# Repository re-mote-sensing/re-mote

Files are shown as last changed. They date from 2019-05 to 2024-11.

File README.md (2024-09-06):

<div align="center">
    <h1>re:mote</h1>
    <p>Open-source Low-cost Software and Hardware Infrastructure for Remote Sensing</p>
</div>

## 📎 Table of Contents

1. [About re:mote](#-about-remote)
2. [LoRa & Mesh Network](#-lora--mesh-network)
3. [Setup](#-get-started)
    - [Water Quality Sensing](#setup-water-quality-sensing)
    - [Turtle Tracker](#setup-turtle-tracker)
4. [Documentation](#-documentation)
5. [Acknowledgement](#-acknowledgment)

## 📒 About re:mote

### Low-cost Water Quality Sensing and Turtle Tracking

This is a software and hardware infrastructure for long-term monitoring of water quality parameters and seasonal monitoring of turtle movements that normally cost a lot more to make, but you can do it by yourself at a fraction of the price compared to commercial products. It supports various configurations, including different sensors, network options, and enclosures, making it adaptable to diverse environments. Designed for low power consumption for 3 months using 6 AA batteries, it can be deployed in a remote area with limited cell connection.

<div align="center">
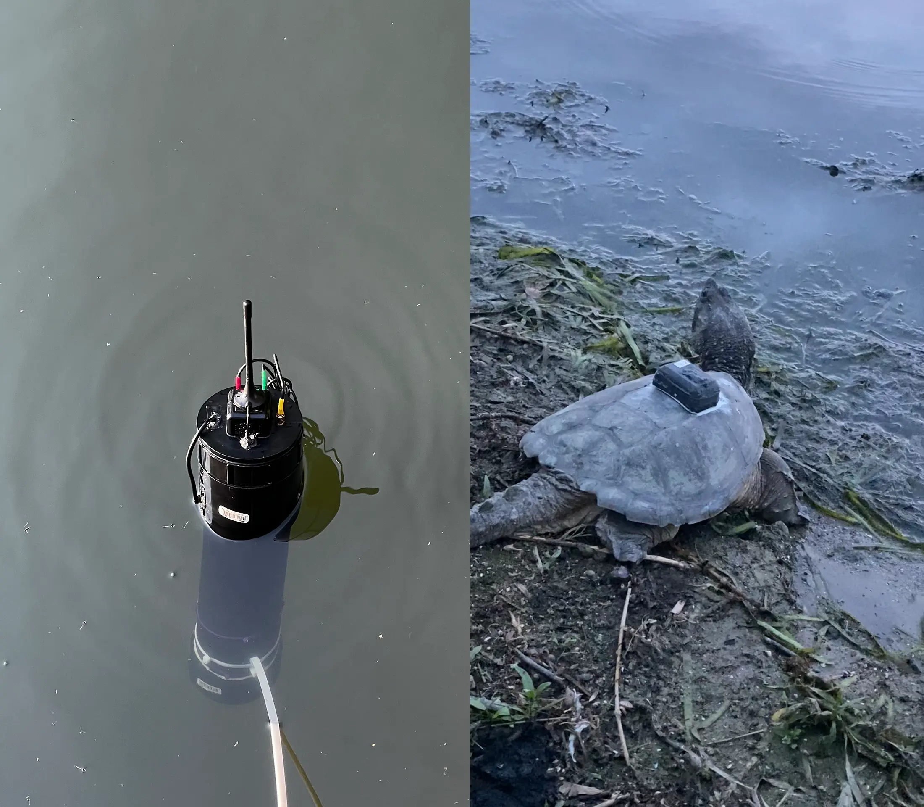
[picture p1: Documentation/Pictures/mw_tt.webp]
    
    <p>Working Water Sensor / Turtle Tracker</p>
</div>

---

## 🛰 LoRa & Mesh Network

### Low-power long-range sensor network

A LoRa mesh network is optionally used for connecting motes (motes can operate standalone).
- It is a low-bandwidth, low-power, and long-range network.
- The mesh network is tolerant to faults, changing network topology, extension, and contraction.

<div align="center">
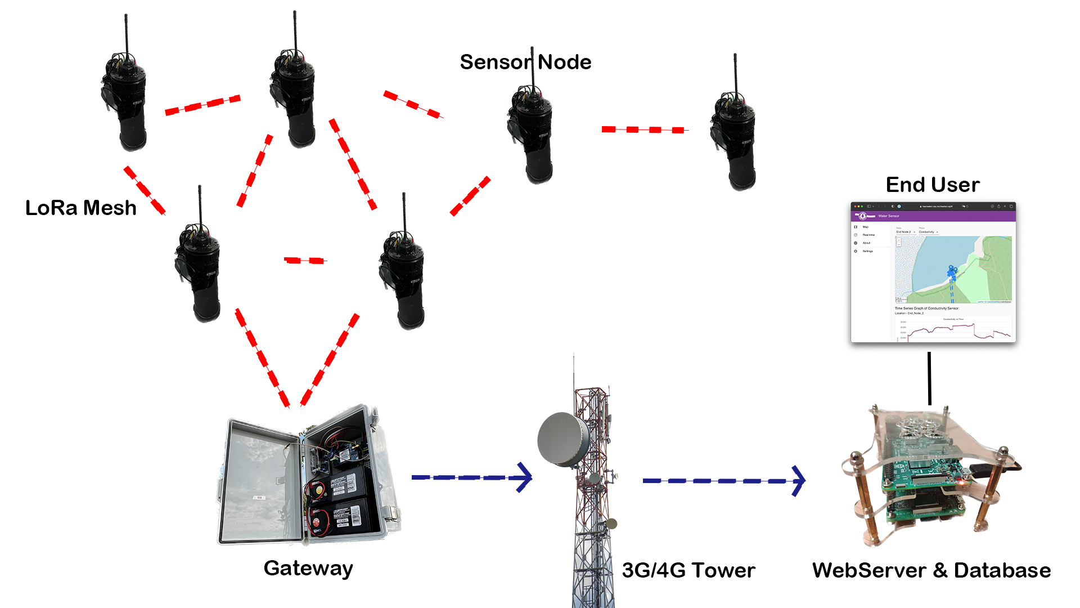
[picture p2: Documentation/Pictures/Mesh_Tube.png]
    
</div>

### Motes

- Mote is an old term for an IoT device which is connected to the network.

Water monitoring network:
- **Gateway** (one or multiple) to relay motes data to the server over the
internet using a CAT-M1/NB-IoT/LTE/3G connection.
- **End Motes** (one or multiple) to measure water quality parameters through attached sensors.
    - **pH** sensor shows the acidity or alkalinity, helping to detect imbalances.
    - **Conductivity** sensor reveals the amount of salts present, providing insight into water quality.
    - **Dissolved Oxygen** sensor measures oxygen levels in the water, indicating the health of aquatic life.
    - **Water Temperature** sensor helps calibrate all sensor levels.
    - **Turbidity** sensor indicates water clarity, with changes signalling potential disturbances.
    - **[Custom sensors](/Documentation/Water_Sensor/Custom_Sensors.md)**

### Server

For real-time monitoring, the Raspberry Pi is an affordable option. However, a regular PC can also be utilized if preferred.

The server is programmed in Golang for fast and concurrent connections.
- A progressive web application designed in React with a custom API.
    - A Progressive Web Application (PWA) enables you to access and browse your data conveniently on your phone.
    - A custom API facilitates easy integration with various other systems.
- A time-series database (InfluxDB) for simple data storage and a smaller footprint. Time series databases assume that insertions are more frequent than queries, so it allows for the fast insertion of large amounts of data, such as water quality data. [Learn More](https://gitlab.cas.mcmaster.ca/re-mote/publications/-/tree/master/FadhelSekerinskiYao18Timeseries)

## 🚀 Get started

This list will guide you step by step to get started.

---

### Setup [Water Quality Sensing](Water_Sensor/)

1. Get all the [hardware](/Documentation/Water_Sensor/Specification.md) you need.

2. Setup a water sensor server with one of the options below. They perform with the same functionality, with docker you do not need to configure all dependencies and run on your own server or computer.
    - Install water sensor server on [Docker](Water_Sensor/re-mote-webserver/). **(Recommended)**
    - Install water sensor server on [Linux](/Documentation/Water_Sensor_Server/Server_Instructions.md).
    - Install water sensor server on a [cloud service](https://gitlab.cas.mcmaster.ca/re-mote/publications/tree/master/HuangMengqi19Encryption&Storage).

3. Assembly of Hardware for the [SensorMotes and/or Gateways](/Documentation/Water_Sensor/Build_a_Water_Sensor_Portal.md).

4. [Testing and Deploying](/Documentation/Water_Sensor/Build_a_Water_Sensor_Portal.md#testing).

---

### Setup [Turtle Tracker](Turtle_Tracker/)

1. Get all the [hardware](Turtle_Tracker/Docs/Specification.md) you need.

2. Setup a water sensor server with one of the options below.
    - Install water sensor server on [Linux](/Documentation/Water_Sensor_Server/Server_Instructions.md) with the [source code](Turtle_Tracker/turtle-tracker-webserver).
    - Install turtle tracker server on a [cloud service](https://gitlab.cas.mcmaster.ca/re-mote/publications/tree/master/HuangMengqi19Encryption&Storage).

3. Assemble Hardware and Upload the Firmware for [Tracker](Turtle_Tracker/Docs/Assembly_of_Trackers.md) and [Gateway](Turtle_Tracker/Docs/Assembly_of_Gateway.md).

---

### Get help

- If you have any questions or encounter issues, post them [here](https://github.com/re-mote-sensing/re-mote/issues).

## 🗂 Documentation

- For developers only.

 - Water Sensor
    - End Mote & Gateway
        - [LoRa message format](/Documentation/Water_Sensor/Message_Formats.md)
        - [Saved data formats](/Documentation/Water_Sensor/Saved_Data_Formats.md)
        - [Add custom sensors](/Documentation/Water_Sensor/Custom_Sensors.md)
    - Server
        - [Jupyter analysis](Jupyter_Analysis/)
        - [REST api](https://documenter.getpostman.com/view/5847961/2s83tDpshb)
        - [Database format](/Documentation/Water_Sensor_Server/Database_Format.md)
 - Turtle Tracker
    - End Mote & Gateway
        - [LoRa message format](Turtle_Tracker/Docs/message_format_turtle_tracker.xlsx)
 - Research
    - [Research documents](Research/)

## 🏆 Acknowledgment

[McMaster University](https://www.mcmaster.ca)

[Global Water Futures](https://gwf.usask.ca)

[MacWater](http://www.macwater.org)

[Ontario Research Fund](https://www.ontario.ca/page/ontario-research-fund)

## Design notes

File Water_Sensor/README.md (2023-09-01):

# re:mote | Water Sensor

## Arduino

`./Node_Code/Node_Code.ino` is the main arduino-based motes firmware.

`./Libraries/` are required libraries for motes.

## Server

`./re-mote-webserver` is the server program running on your PC or cloud service to provide real-time motinoring.

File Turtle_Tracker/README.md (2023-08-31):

turtle

# Turtle Tracker Overview

Code used in the Turtle Tracker project, 2022 version. This version differs from the previous version located in `Node_Code.ino`.

## Arduino Code

`./Arduino_Code/Gateway_Code/` is for use with the Gateway module which consists of an Arduino UNO, LoRA shield, 3G Shield and SD Card Reader.

`./Arduino_Code/Tracker_Code/` is for use with the Turtle Tracker module which consists of a Moteino (RFM95) and GPS module.

## Documentations

 - [Hardware Specification](./Docs/Specification.md)

###### Setup:

 - [Assembly of Gateway](./Docs/Assembly_of_Gateway.md)

 - [Assembly of Trackers](./Docs/Assembly_of_Trackers.md) | [Trackers Enclosure](./Docs/3D_Printed_Enclosure/README.md)

 - [Pi Server Source Code](./turtle-tracker-webserver) | [How to Setup Server](/Documentation/Water_Sensor_Server/Server_Instructions.md)

###### Code:

 - [Message Format](./Docs/message_format_turtle_tracker.xlsx)

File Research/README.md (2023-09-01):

# Research Projects
## AnjaliNarayanan18
Testing code on temperature and turbidity sensors.
## HassanElaghoury18
Testing code on LoRa mesh network.
## LoRa
Selection of LoRa modules, LoRa range test and testing code on LoRa mesh network.
## MingzheAES
Research on AES Encryption
## Ryan_Notes
Notes on turtle tracker (GPS, LoRa, Antenna, Microcontroller, Enclosure).
## Server_design
Server design notes

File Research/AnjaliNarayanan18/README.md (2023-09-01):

Testing code on temperature and turbidity sensors.

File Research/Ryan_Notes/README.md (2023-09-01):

Notes on turtle tracker (GPS, LoRa, Antenna, Microcontroller, Enclosure).

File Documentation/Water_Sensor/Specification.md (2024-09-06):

# Specification for Water Quality Sensing

## Server Node

Raspberry Pi is the inexpansive option, any PC that runs Docker can be used (Windows, Linux, MacOS).

| Part           | Link                                                         |
| -------------- | ------------------------------------------------------------ |
| Raspberry Pi 4 | https://www.raspberrypi.com/products/raspberry-pi-4-model-b/ |
| SD card 32 GB *  | https://www.amazon.ca/gp/product/B08GY9NYRM/                 |

* You have the flexibility to use various SD cards; here's an example for reference.

<br><br>

## Water Sensor End Node

| Part                            | Link                                                               |
| ------------------------------- | ------------------------------------------------------------------ |
| Arduino Mega                    | https://www.amazon.ca/gp/product/B01H4ZDYCE/                       |
| MicroSD Card *                  | https://www.amazon.ca/gp/product/B08J4HJ98L/                                     |
| MicroSD Card Reader Module      | https://www.amazon.ca/gp/product/B07GXBP672/                                     |
| AA Battery Holder (3 x 1.5v) *  | https://www.amazon.ca/gp/product/B07PJT5NHL/                       |

* You're not limited to a specific SD card; here's an example for your consideration. However, it's essential to note that the SPI card reader lacks error correction. To mitigate potential issues, opt for a reputable, high-quality brand.
* You can explore alternative battery options, provided the voltage falls within the 4.5 to 5.5V range.

| Part                            | Link                                                               |
| ------------------------------- | ------------------------------------------------------------------ |
| GPS Receiver - GP-735           | https://www.sparkfun.com/products/13670                            |
| JST connector (for GPS)         | https://www.digikey.ca/en/products/detail/sparkfun-electronics/PRT-10361/6605206 |

* GPS is optional, if you prefer to enter coordinates by yourself

## Sensors

| Part                    | Link                                                               |
| ----------------------- | ------------------------------------------------------------------ |
| Conductivity Kit        | https://atlas-scientific.com/kits/conductivity-k-0-1-kit/          |
| Dissolved Oxygen Kit    | https://atlas-scientific.com/kits/dissolved-oxygen-kit/            |
| Turbidity Sensor        | https://www.dfrobot.com/product-1394.html                          |
| Temperature Sensor Kit  | https://www.dfrobot.com/product-1354.html                          |
| Industrial pH Probe<br><br>EZO™ Carrier Board for pH<br><br>EZO™ pH Circuit     | https://atlas-scientific.com/probes/industrial-ph-probe/<br><br>https://atlas-scientific.com/carrier-boards/electrically-isolated-ezo-carrier-board-gen-2/<br><br>https://atlas-scientific.com/embedded-solutions/ezo-ph-circuit/|

- It's recommended to use one or more specified sensors. However, if you opt for alternative sensors, be aware that programming skills are necessary for proper integration.

### Additional Hardware
Depending on your network preference, select one of the options provided below.

---

<details>
<summary>Using LoRa with one or more gateways</summary>
<br>

This approach employs a mesh network, ideal for situations where the 3G signal is unstable or unavailable over water.

<div align="center">
    
</div>

A gateway is essential to facilitate the transmission of data from the node to the server.

## Water Sensor End Node with **LoRa** Additional Components

| Part                    | Link                                                               |
| ----------------------- | ------------------------------------------------------------------ |
| Mesh LoRa [YL-800N Datasheet](/Documentation/Datasheets/LoRa_MESH_Radio_YL-800N_EN.pdf)               | https://www.dfrobot.com/product-1670.html                          |

<br>

## Water Sensor Gateway Node (Only if using LoRa on End Node)

| Part                                        | Link                                                                             |
| ------------------------------------------- | -------------------------------------------------------------------------------- |
| Arduino Uno *                               | https://www.canadarobotix.com/products/60                                        |
| 3G Shield *                                 | https://www.tinyosshop.com/3g-gprs-gsm-shield-for-arduino-sim5320a               |
| Mesh LoRa                                   | https://www.dfrobot.com/product-1670.html                                        |
| MicroSD Card *                              | https://www.amazon.ca/gp/product/B08J4HJ98L/                                     |
| MicroSD Card Reader Module *                | https://www.amazon.ca/gp/product/B07GXBP672/                                     |
| DHT Sensor                                  | https://www.amazon.ca/gp/product/B07CM2VLBK/                                     |
| SIM Card with data plan (120 days) *        |                                                                                  |

* Other Arduino based board also works.
* Depending on your location or country, you may require a different version of the 3G shield that is compatible with your SIM card.
* You're not limited to a specific SD card; here's an example for your consideration. However, it's essential to note that the SPI card reader lacks error correction. To mitigate potential issues, opt for a reputable, high-quality brand.
* As of 2023 in Canada, Virgin/Fido offers a $10 tablet plan that aligns well with the requirements of this project. Alternatively, considering an IoT SIM card could also be an effective solution.

</details>

---

<details>
<summary>Using 3G on sensor node without gateway</summary>
<br>

This approach involves equipping all sensor nodes with 3G connectivity. It's ideal for setups where all nodes are within areas with available 3G signal and are spaced at considerable distances from one another.

<div align="center">
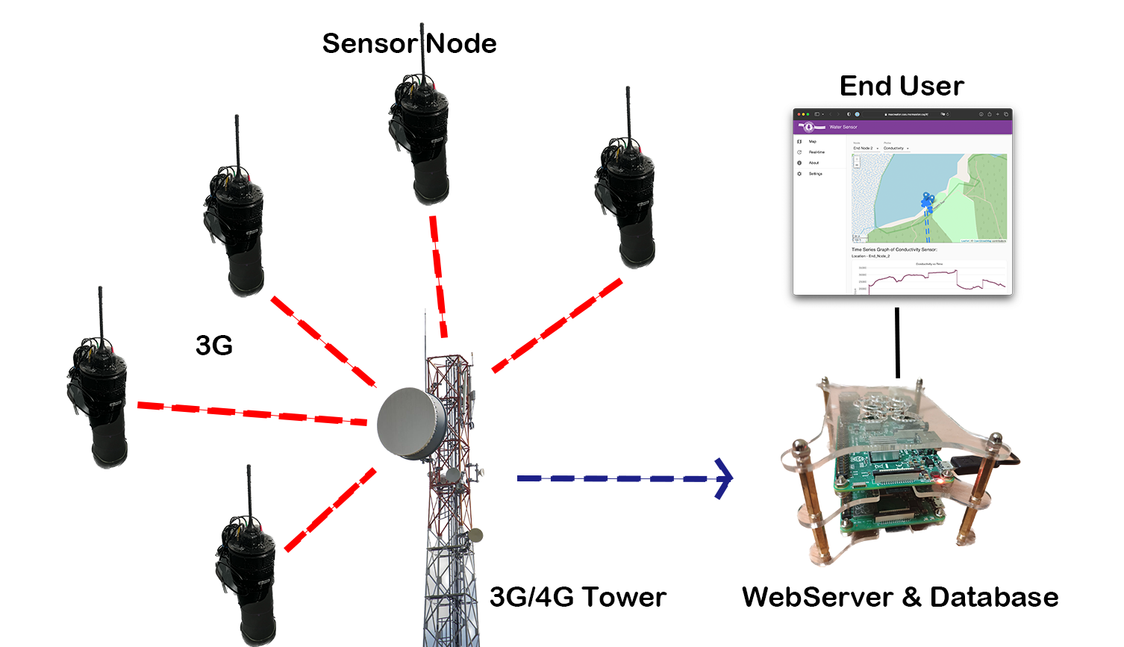
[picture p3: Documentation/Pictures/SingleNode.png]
    
</div>

## Water Sensor End Node with **3G** Additional Components

| Part                    | Link                                                               |
| ----------------------- | ------------------------------------------------------------------ |
| 3G Shield *                                 | https://www.tinyosshop.com/3g-gprs-gsm-shield-for-arduino-sim5320a               |
| SIM Card with data plan (120 days) *        |                                                                                  |

* Depending on your location or country, you may require a different version of the 3G shield that is compatible with your SIM card.
* As of 2023 in Canada, Virgin/Fido offers a $10 tablet plan that aligns well with the requirements of this project. Alternatively, considering an IoT SIM card could also be an effective solution.

</details>

---

<details>
<summary>Using as a data logger and store data on the SD card without uploading to server</summary>
<br>

This option is suitable if you don't require real-time data and prefer to retrieve information solely from an SD card.

<div align="center">
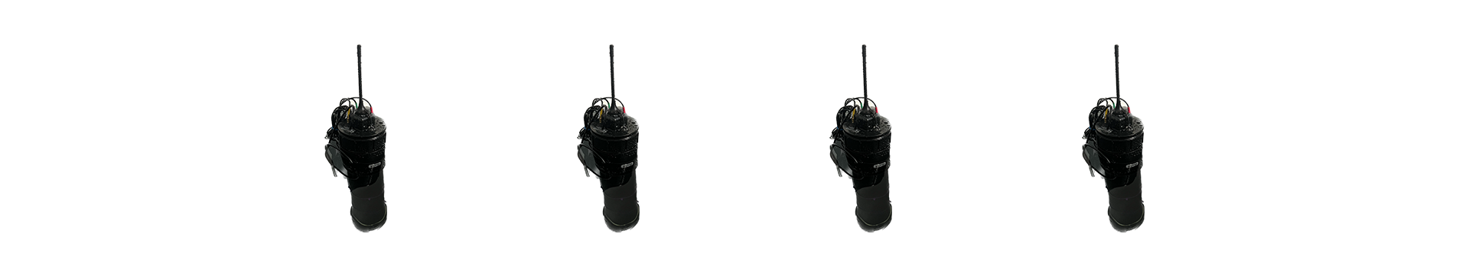
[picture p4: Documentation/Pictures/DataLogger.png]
    
</div>

No additional hardware is needed.

</details>

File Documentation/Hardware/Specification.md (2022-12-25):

# Specification for Water Quality Sensing 

**Last updated:** Oct 24, 2022 by [Tianyu Zhou](https://gitlab.cas.mcmaster.ca/KrunkZhou)

## Water Sensor End Node

| Part                    | Link                                                               |
| ----------------------- | ------------------------------------------------------------------ |
| Arduino Nano            | https://www.amazon.ca/gp/product/B0097AU5OU/                       |
| Mesh LoRa               | https://www.dfrobot.com/product-1670.html                          |
| Breadboard PCB          | https://www.amazon.ca/gp/product/B00SK8QR8S/                       |
| Conductivity Kit        | https://atlas-scientific.com/kits/conductivity-k-0-1-kit/          |
| Dissolved Oxygen Kit    | https://atlas-scientific.com/kits/dissolved-oxygen-kit/            |
| Turbidity Sensor        | https://www.dfrobot.com/product-1394.html                          |
| Temperature Sensor Kit  | https://www.dfrobot.com/product-1354.html                          |
| Industrial pH Probe     | https://atlas-scientific.com/probes/industrial-ph-probe/           |
| EZO™ Carrier Board for pH | https://atlas-scientific.com/carrier-boards/electrically-isolated-ezo-carrier-board-gen-2/ |
| EZO™ pH Circuit         | https://atlas-scientific.com/embedded-solutions/ezo-ph-circuit/    |
| GPS Receiver - GP-735   | https://www.sparkfun.com/products/13670                            |
| JST connector (for GPS) | https://www.digikey.ca/en/products/detail/sparkfun-electronics/PRT-10361/6605206 |

## Water Sensor Gateway Node

| Part                                        | Link                                                                             |
| ------------------------------------------- | -------------------------------------------------------------------------------- |
| Arduino Uno                                 | https://www.canadarobotix.com/products/60                                        |
| 3G Shield                                   | https://www.tinyosshop.com/3g-gprs-gsm-shield-for-arduino-sim5320a               |
| Mesh LoRa                                   | https://www.dfrobot.com/product-1670.html                                        |
| MicroSD Card                                | https://www.amazon.ca/gp/product/B08J4HJ98L/                                     |
| MicroSD Card Reader Module                  | https://www.amazon.ca/gp/product/B07GXBP672/                                     |
| DHT Sensor                                  | https://www.amazon.ca/gp/product/B07CM2VLBK/                                     |
| SIM Card with data plan (120 days)          |                                                                                  |

## Server Node

| Part           | Link                                                         |
| -------------- | ------------------------------------------------------------ |
| Raspberry Pi 4 | https://www.raspberrypi.com/products/raspberry-pi-4-model-b/ |
| SD card 32 GB  | https://www.amazon.ca/gp/product/B08GY9NYRM/                 |

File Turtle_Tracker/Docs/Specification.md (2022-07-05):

# Specification

**Last updated:** July 1, 2022 by [Tianyu Zhou](https://gitlab.cas.mcmaster.ca/KrunkZhou)

## Turtle Tracker Remote Node

| Part                                        | Link                                                                             |
| ------------------------------------------- | -------------------------------------------------------------------------------- |
| GPS receiver                                | https://www.sparkfun.com/products/13670                                          |
| Moteino (trace antenna) + RFM95 LoRa Module | https://lowpowerlab.com/shop/product/145                                         |
| JST connector (for GPS)                     | https://www.digikey.ca/en/products/detail/sparkfun-electronics/PRT-10361/6605206 |
| JST PH 2-Pin Male Header Cable              | https://bc-robotics.com/shop/jst-ph-2-pin-cable-male-conenctor/                  |
| 3.7V 1600mAh Li-Po Battery                  | https://www.amazon.ca/gp/product/B091XYZ2V3/                                     |

#### Enclosure

| Part          | Link                                         |
| ------------- | -------------------------------------------- |
| PETG Filament | https://www.amazon.ca/gp/product/B07PGYHYV8/ |
| Screws        | https://www.homedepot.ca/product/1000141168  |

## Turtle Tracker Gateway Node

| Part                    | Link                                                               |
| ----------------------- | ------------------------------------------------------------------ |
| Arduido UNO             | https://www.canadarobotix.com/products/60                          |
| Tinysine 3G Shield      | https://www.tinyosshop.com/3g-gprs-gsm-shield-for-arduino-sim5320a |
| LoRa Shield             | https://www.amazon.ca/gp/product/B07HD1MH3J/                       |
| LoRa Antenna 8dBi       | https://www.amazon.ca/gp/product/B09N27QPRX/                       |
| SD Card 32G             | https://www.amazon.ca/gp/product/B08J4HJ98L/                       |
| SD Card Reader          | https://www.amazon.ca/gp/product/B07GXBP672/                       |
| GPIO Cable              | https://www.amazon.ca/gp/product/B01EV70C78/                       |
| Battery                 |                                                                    |
| Solor Panel             |                                                                    |
| SIM Card with Data Plan |                                                                    |

#### Enclosure

| Part                    | Link                                         |
| ----------------------- | -------------------------------------------- |
| Box                     | https://www.amazon.ca/gp/product/B083R8X4RT/ |
| Solar Cable Entry Gland | https://www.amazon.ca/gp/product/B09G6LXDSS/ |

## Turtle Tracker Server Node

| Part           | Link                                                         |
| -------------- | ------------------------------------------------------------ |
| Raspberry Pi 4 | https://www.raspberrypi.com/products/raspberry-pi-4-model-b/ |
| SD card 32 GB  | https://www.amazon.ca/gp/product/B08GY9NYRM/                 |

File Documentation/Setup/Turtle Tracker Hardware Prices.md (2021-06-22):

# Prices for Turtle Tracker hardware
### Last updated: June 22, 2021

**Moteino Microcontroller + RFM95 LoRa module** \
**Price**: $33.87 CAD \
[Order Link: LowPowerLab](https://lowpowerlab.com/shop/product/145)

**GP-735 GPS Module** \
**Price: Digikey**: $63.71 CAD \
**Price: Mouser**: $63.41 CAD \
**Price: Elmwood Electronics**: $70.99 CAD \
**Price: Sparkfun**: $56.63 CAD \
[Order Link: Digikey](https://www.digikey.ca/en/products/detail/sparkfun-electronics/GPS-13670/6578384?s=N4IgjCBcoLQBxVAYygMwIYBsDOBTANCAPZQDa4ArAGwIC6AvvYQExkgDiACgMoxgDMVAOwAGEAyA)\
[Order Link: Mouser](https://www.mouser.ca/ProductDetail/?qs=WyAARYrbSnYtKgB69l%252B%252BDA==)\
[Order Link: Elmwood Electronics](https://elmwoodelectronics.ca/products/13670)\
[Order Link: Sparkfun](https://www.sparkfun.com/products/13670)

**JST connector (for GPS)** \
**Price**: $1.95 CAD \
[Order Link: Digikey](https://www.digikey.ca/en/products/detail/sparkfun-electronics/PRT-10361/6605206)

**3.7V 400mAh Li-Po Battery**
**Price**: $6.99 CAD
[Order Link: Canada Robotix](https://www.canadarobotix.com/products/940)

**JST PH 2-Pin Male Header Cable**
**Price**: $1.95 CAD
[Order Link: BC Robotics](https://bc-robotics.com/shop/jst-ph-2-pin-cable-male-conenctor/)

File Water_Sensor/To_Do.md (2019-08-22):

# List of things to do on this project

This is a list of things that need to be done in this project, in no particular order

* Turn this list into gitlab issues
* Create file detailing how to setup turtle trackers
* Split water quality setup file into end node, gateway, and server setup files
* Do a proper deployment test
* Add some form of testing and calibration code to make seting up things easier for others
* Add proper backwards communication (from server to gateway to end node) for changing settings
* Convert to new lower power Arduinos
* Add ability to change settings using bluetooth
* Convert Arduino code to use an event loop
* Add remoteConfig.h configurator to the website to make configuration a lot easier
* Robustify both the Gateway and End Node to ensure proper handling of errors
* Add ability to send error to website from node
* Add ability to change the time period that you're viewing data for to the website
* Add encryption for messages between nodes
* Add encryption to saved data on server
* Add ability to add login page to view data on the website, maybe with different amounts of power (ex: view data vs. change node settings)
* Add verification to ensure that data coming from an end node is legitimate, same for gateway to server
* Document how to change all modules on nodes (ex: data saving, communication method, etc.)
* Add data point validation to the server (remove outliers)
* Add website alerts for important data changes (spikes, dips, etc.)
* Add data analysis capabilities to the website
* Fix floating point rounding causing weird values
* Change names in data post to gateway to use actual chars instead of hex representation of chars
* Combine similar libraries from Libraries\_Victor and Libraries\_Ryan together
	* Namely the EndData/EEPROM, Sleep/LowPower, and GPS/UBX+NeoGPS libraries
* Add one time 3G module setup code to gateway
	* .setGPRSNetworkSettings("pda.bell.ca");
	* .setHTTPSRedirect(true);

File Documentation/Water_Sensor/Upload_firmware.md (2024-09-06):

## The Software You Need

### Arduino IDE

First, download and install the [Arduino IDE](https://www.arduino.cc/en/main/software) available on Windows, Linux and MacOS. This software allows you to upload code from your computer to the Arduino-compatible microcontroller. Alternatively, you can use the Arduino web editor or any other IDE that supports uploading .ino files to Arduino devices.

### Program file

Next, download the [Node_Code.ino](/Water_Sensor/Node_Code/Node_Code.ino) file from the provided repository. This file contains the primary program that will execute on the Arduino.

### Libraries

Next, you'll need to incorporate the required libraries. Start by downloading all the library files from the [Libraries](/Water_Sensor/Libraries/) directory of this repository. Once downloaded, copy all the files into your [Arduino library folder](https://www.arduino.cc/en/guide/libraries).

- Windows: /Users/{username}/Documents/Arduino/libraries/
- Linux: /home/{username}/Arduino/libraries/
- Mac: ~/Documents/Arduino/libraries/

Replacing what is already there (if anything).

### Select the development board

#### Using Arduino Mega

Select `Tools -> Board -> Arduino AVR Boards -> Arduino Mega` from the top bar.

#### Using Moteino Mega

Install the `Moteino AVR Boards` package in Arduino IDE: [Programming & Libraries](https://lowpowerlab.com/guide/moteino/programming-libraries/).

Select `Tools -> Board -> Moteino AVR Boards -> Moteino Mega` from the top bar.

---

Connect the Arduino to the computer by USB cable or FTDI cable.

Open `Node_Code.ino` in Arduino App.

## Upload

Upload with Arduino IDE by clicking the upload (->) button.

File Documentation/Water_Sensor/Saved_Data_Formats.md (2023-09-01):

# Saved Data Formats for Arduino End Node and Gateway node, and Raspberry Pi Server

This file contains some specification on the different formats in which data is saved on the Arduino end nodes and gateway nodes, and on the Raspberry Pi server.

## Arduino End Node

The format that the Arduino end node uses to save the time, location, and sensor data in its EEPROM. If the EEPROM on the Arduino that you are using has been used before, make sure to set the first 4 bytes according to the default values of Last Saved Data Address and Valid Data From Address. The format of the data is as follows: 

| **Description**   | Last Saved Data Address | Valid Data From Address | Data Points |
|-------------------|-------------------------|-------------------------|-------------|
| **Size in Bytes** | 2                       | 2                       | (1 + 4 * (Number of sensors + 1)) * Number of data points + 8 * Number of locations |
| **Contents**      | The EEPROM address directly after the end of the last saved data point. Default value is 4 | The EEPORM address where valid data starts. Default value is 3 | The actual saved data |

The last column is described below:

| **Description**   | Has Location | Time | Location       | Sensor Data           |
|-------------------|--------------|------|----------------|-----------------------|
| **Size in bytes** | 1            | 4    | 8 if it exists | 4 * Number of sensors |
| **Contents**      | Byte representing whether or not this data point contains location data | An unsigned integer (32 bit) representing the Unix time that this data was collected at | Two 4 byte floats, the first represents latitude, the second longitude. If this data point doesn't contain location data, this is 0 bytes long | A float representing the data collected from a sensor. This column is repeated for every sensor on the end node |

A data point will only include a location if the location of the end node has changed by more than 0.00005 degrees [(~5.57 m)](https://en.wikipedia.org/wiki/Decimal_degrees#Precision) in either latitude or longitude (due to inaccuracies in GPS modules). The data will loop around the EEPROM if it's necessary, overwriting the oldest data with new data.

<br/>

**Storage size:**  
The number of data points the EEPROM will be able to hold depends on the Arduino being used, the number of sensors, and how frequently the location is changing, but can be calculated using the following formula, where the things in the square brackets must be replaced:  
(\[EEPROM size\] - 4) / (1 + (\[Number of sensors\] + 1) * 4 + \[Fraction of data points that contain a location\] * 8)  
As an example, if we used an Arduino nano (1KB EEPROM) with 4 sensors, reading the sensors every hour, and assume the location is going to change once every 48 sensor reads (2 days), we get:  
(1024 - 4) / (1 + (4 + 1) * 4 + 1/48 * 8) = 48.19 data points, or 2 days of internal data storage

<br/>

**Rationale:**  
The reason behind most of these design decisions is storage space availability; Arduinos generally have very little EEPROM (aswell as SRAM and Flash) memory, thus storage space conservation is very important. With the EEPROM, we encounter another problem; that is that the EEPROM can only be written to quite a low amount of times (100000) before it could start to fail. Taking these two factors into account, I designed the overhead space usage to be quite low (only 4 bytes), and tried to minimize the space required by each data point on average. Using a "has location" byte reduces the amount of memory each data point uses on average (as long less than 7/8 of data points have a location), while still being able to easily add or remove data points. The use of two addresses for "bookkeeping" allows easily writing/reading the important data and looping around the EEPROM, without excessive EEPROM writes.

<br/>

## Arduino Gateway Node

The format that the Arduino gateway node uses to save the time, location, and sensor data from multiple nodes in its SD card. Please supply the gateway node with a completely empty SD card (or microSD), formatted to either Fat16 or Fat32.  
Each node registered with the gateway node has its own .csv file on the SD card named nodeX.csv (where X is the node's id). The format for that .csv is as follows, where things in brackets are replaced by actual data: 

(Name of node)  
Time, Latitude, Longitude, (Sensor 1 Name), (Sensor 2 Name) ...  
(Data 1 Time), (Data 1 Latitude), (Data 1 Longitude), (Data 1 Sensor 1), (Data 1 Sensor 2) ...  
(Data 2)  
...

**Example:**  
ITB\_TEST  
Time, Latitude, Longitude, Temperature, Dissolved\_Oxygen, Turbidity, Conductivity  
1560443510000000000,43.259397,-79.920138,17.4,7.89,13,52.25  
1560443556000000000,,,16.8,8.07,4,0  
1560690552000000000,,,17.3,8.11,7,104.3  

The node can have any number of sensors (although the LoRa message formats limit this to 15), it can have any number of data points, and all of the names can be of any size (but cannot contain commas or new lines). Time is the string representation of an unsigned integer (32 bit) of the unix time that the data point was collected at, Latitude and Longitude are the string representations of floats of the latitude and longitude of the node, and the sensor data is the string representation of a float of the data collected for that sensor. Please note: not every data point in the file will have a latitude and longitude, they are only inserted if the node's location changes.

<br/>

There is then an additional .csv on the SD card named ToSend.csv, which contains data on what node data still needs to be posted to the server. Its format is as follows, again where things in brackets are replaced by actual data:

Node ID, Data Points, Locations, Position  
(Node 1 ID), (Number of data points node 1 has to send), (Number of data points that have a location), (Position in the node 1 file where the data to be sent starts)  
(Node 2)  
...

**Example:**  
Node ID, Data Points, Locations, Position  
2,002,001,48  
4,003,000,763  
3,001,001,104

Both the ID and position in the file are printed as whatever length, but the number of data points and the number of locations are always printed as 3 digit numbers (using leading zeros if needed). Please note: Only nodes that have data to send to the server will have data in this file, and a node cannot have more than 255 data points or locations waiting to be sent to the server.

<br/>

**Storage size:**  
The amount of data the SD card will be able to hold depends on a lot of different factors, especially how often the location is updated and which sensors are being used, as this can influence how many characters are required for each data point (7.1 vs 982.3465; both are floats but take up very different amount of memory when printed as a string)  
As a quick example, let's assume 5 end nodes with 4 sensors each sending data every hour, and their locations changing every 48 hours. Let's also assume names (node and sensor) of 15 characters, each sensor reading takes 5 characters (ex: 54.89), time takes 10 characters (ex: 1561405722), and each of latitude and longitude take 10 characters (ex: -79.920551). For a 2GB microSD card (ignoring flash overhead space loss), we get:  
(2*10^9) - 5 * (16 + 34 + 15 * 4) = 1999999450 bytes of memory available for data storage (ignoring ToSend.csv, as it takes very minimal space)  
We then get that each data point takes:  
13 + 10 + 4 * 5 + (1/48) * 20 = ~43.42 bytes  
This gives us:  
1999999450 / 43.42 = ~46061710 data points, or ~9212342 data points per node, or ~383847.6 days of data storage.  

<br/>

**Rationale:**  
As can be seen, saving space is much less important when dealing with the SD card on the gateway node. That is why I was able to take some liberties to make data reading, writing, and analizing easier. This includes using the .csv format, which can take extra overhead space with the commas, but allows for easy importing into excel, which could be very useful for daa analysis. It also allowed using strings for saving the data, making it much easier for humans to read it. It also allowed saving a bit of extra data in ToSend.csv (number of data points and number of locations), which aren't strictly necessary, but allows the gateway Arduino to quickly get the size required for the data post to the server before constructing the post, which stops [heap fragmentation](https://cpp4arduino.com/2018/11/06/what-is-heap-fragmentation.html).

<br/>

## Raspberry Pi Sever

The format that the Raspberry Pi server uses to save the time, location, and sensor data from multiple nodes in its InfluxDB database (default name is MacWater). The database has two measurements (tables) named sensorInfo and sensorMeasurements. sensorInfo looks like: 

| **time** | **id** | **name** | **value** |
|----------|--------|----------|-----------|

In this case, value is a string representing the latitude and longitude of the node (ex: "43.258506,-79.920547"). This table is used to keep tack of the nodes' names and locations, their "info". Every entry in the table represents a location change, and must contain a time, id, and value. The name column only needs to be filled once per node id. Every column in this table is represented as a string

<br/>

sensorMeasurements looks like: 

| **time** | **id** | **sensortype** | **value** |
|----------|--------|----------------|-----------|

This table is used to log the actual sensor data from the nodes. Each entry in this table represents a sensor reading, and must contains a time, id, sensortype, and value. The id and sensortype columns are represented as strings, whereas value is a float.

<br/>

**Rationale:**  
By using two tables, we are able to separate node information data that will probably be updated infrequently and the sensor data that will be updated very frequently. The data from the two tables can still be linked together quite easily using the node's id.

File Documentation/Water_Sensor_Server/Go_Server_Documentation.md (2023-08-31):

# Go Influxdb API Documentation

Wherever {Homepage} is written it means the main URL that your server is running on (ex: [http://www.cas.mcmaster.ca/](http://www.cas.mcmaster.ca/#)).

## Getting node information

### Getting current information of nodes

**Type:** GET  
**URL:** {Homepage}/sensor/info  
**Description:** Gets the current information of all sensors, including id, name, last known coordinates, and time of those coordinates  
**Example:** {Homepage}/sensor/info  
Could return:

		{  
			"locations": [  
				[  
					"1",  
					"itb",  
					"43.259009, -79.920048",  
					"1557168840530000000"  
				],  
				[  
					"2",  
					"McMaster_Innovation_Park",  
					"43.256857, -79.900731",  
					"1557238174630000000"  
				],  
				[  
					"3",  
					"GPS",  
					"43.261032, -79.907221",  
					"1557238177230000000"  
				]  
			]  
		}  

### Getting detailed information of a specific node

**Type:** GET  
**URL:** {Homepage}/sensor/info?id={id}  
**Description:** Gets the entire location information of the node with id {id}  
**Example:** {Homepage}/sensor/info?id=3  
Could return:

		{  
			"name": "GPS",  
			"locations": [  
				[  
					"1557238176630000000",  
					"43.260948, -79.907204"  
				],  
				[  
					"1557238177230000000",  
					"43.261032, -79.907221"  
				]  
			]  
		}  

### Getting current information of all nodes with a certain sensor type

**Type:** GET  
**URL:** {Homepage}/sensor/info?type={sensor type}  
**Description:** Gets the current information of all sensors that have data for {sensor type}, including id, name, last known coordinates, and time of those coordinates  
**Example:** {Homepage}/sensor/info?type=Temperature  
Could return:

		{  
			"locations": [  
				[  
					"1",  
					"itb",  
					"43.259009, -79.920048",  
					"1557168840530000000"  
				],  
				[  
					"2",  
					"McMaster_Innovation_Park",  
					"43.256857, -79.900731",  
					"1557238174630000000"  
				]  
			]  
		}  

<br/>

## Getting sensor type information

### Getting sensor types

**Type:** GET  
**URL:** {Homepage}/sensor/type  
**Description:** Gets the full list of sensor types available  
**Example:** {Homepage}/sensor/type  
Could return:

		{  
			"types": [  
				"Temperature",  
				"Turbidity",  
				"Conductivity"
			]  
		}  

### Getting the sensor types available to a specific node

**Type:** GET  
**URL:** {Homepage}/sensor/type?id={id}  
**Description:** Gets the full list of sensor types available for the node with id {id}  
**Example:** {Homepage}/sensor/type?id=1  
Could return:

		{  
			"types": [  
				"Temperature",  
				"Turbidity"  
			]  
		}  

<br/>

## Posting sensor information

**Type:** POST  
**URL:** {Homepage}/sensor/info?id={id}&name={name}&coords={coordinates as a string}&time={unix time in ns}  
**Description:** Adds information data for a node to the database with the above values  
**Example:** {Homepage}/sensor/info?id=1&name=itb&coords=43.259015,-79.920087&time=1562178587000000000  
This request doesn't return any data  

<br/>

## Getting sensor data

### Getting data for a specific node and sensor type

**Type:** GET  
**URL:** {Homepage}/sensor/data?id={id}&type={sensor type}  
**Description:** Gets the data of type {sensor type} from the node with id {id}  
**Example:** {Homepage}/sensor/data?id=1&type=Temperature  
Could return:

		{  
			"id": "1",  
			"type": "Temperature",  
			"data": [  
				[  
					"1557169056986000000",  
					"20"  
				],  
				[  
					"1557169061851000000",  
					"21"  
				],  
				[  
					"1557169065664000000",  
					"18"  
				]  
			]  
		}  

### Getting data for a specific node and sensor type and time interval

**Type:** GET  
**URL:** {Homepage}/sensor/data?id={id}&type={sensor type}&start={unix time in ns}&end={unix time in ns}  
**Description:** Gets the data of type {sensor type} from the node with id {id} where the time is between the start and end times  
**Example:** {Homepage}/sensor/data?id=1&type=Temperature&start=1557169056986000000&end=1557169065543000000  
Could return:

		{  
			"id": "1",  
			"type": "Temperature",  
			"data": [  
				[  
					"1557169061851000000",  
					"21"  
				]  
			]  
		}  

<br/>

## Posting sensor data

### Posting sensor data

**Type:** POST  
**URL:** {Homepage}/sensor/data?id={id}&type={sensor type}&value={value}&time={unix time in s}  
**Description:** Adds sensor data to the database with the above values  
**Example:** {Homepage}/sensor/data?id=1&type=Temperature&value=17.5&time=1562178587  
This request doesn't return any data  

### Posting data and information from multiple nodes

**Type:** POST  
**URL:** {Homepage}/sensor/data?data={data}  
**Description:** Adds sensor and information data from multiple nodes to the database all at once. This is the request that the Arduino gateway nodes use to interact with the web server. Specifications and examples on how to format {data} can be found in the [Arduino message format specification file](/Documentation/Water_Sensor/Message_Formats.md#data-post-to-server).

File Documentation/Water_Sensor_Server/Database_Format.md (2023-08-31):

# InfluxDB format specification

Whenever I write table, I mean an influx measurement.

The database we are using is called MacWater, and contains two tables to save the sensor and node data:

## sensorInfo table

This table has 4 columns: time, id, name, and value, where value represents the coordinates of that node at that time. id, name, and value are all stored as strings.

#### Example: 

|**time**|**id**|**name**|**value**|
|----|--|----|-----|
1455396460000000000| 2 |    West Pond |      43.2697, -79.9318|
1455396485000000000| 2 |    West Pond |      43.2684, -79.9361|
1561742252000000000| 16|    Other     |      43.000000,-79.000000|
1561742334000000000| 16|    Other     |      43.000000,-79.000000|
1563816848000000000| 8192|  Weekend_Gateway| 43.000000,-79.000000|
1564688848000000000| 4112|  Gateway_2|       43.258415,-79.920830|

## sensorMeasurements table

This table has 4 columns: time, id, sensortype, and value, where value is the measurement of that sensortype from that node at that time. id and sensortype are saved as strings, and value is saved as a float.

#### Example:

|**time**|**id**|**sensortype**|**value**|
|----|--|----|-----|
1455592250590000000| 2|     Dissolved_Oxygen|  7.4|
1455652663551000000| 2|     Dissolved_Oxygen|  7.24|
1561742252000000000| 16|    Conductivity    |  487.1|
1561742252000000000| 16|    Dissolved_Oxygen|  7.75|
1561742252000000000| 16|    Turbidity       |  46|
1561742252000000000| 16|    Water_Temperature| 23|
1563816787000000000| 4112|  Air_Temperature|   24.3|
1563816787000000000| 4112|  Humidity       |   57.3|

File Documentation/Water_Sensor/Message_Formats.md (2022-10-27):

# Message Formats for Arduino End Node and Gateway node

This file contains some specification on the different message types that are exchanged between the Arduino end nodes, gateway nodes, and raspberry pi server. The specifications for the LoRa messages are only for the payload portion of the [LoRa mesh modules](https://www.dfrobot.com/product-1670.html) message (the only part we can control). For the specifications of the other parts of the messages, see [Spencer Park's write-up](https://gitlab.cas.mcmaster.ca/re-mote/arduino-motes/blob/master/LoRa/LoRa.ipynb). This document shows that the maximum payload size for the LoRa mesh modules is 111 bytes (127 byte message size - overhead), which gives us very limited space per LoRa message, and considering the current draw of the modules can spike up to 100 mA, keeping the number of messages to a minimum is ideal.

**NOTE:** Arduinos are little endian, so the multi-byte data types may seem "backwards"

## Registration

First message sent from an end node to the gateway node, sent only once and used to register the name and sensor types of an end node with a gateway node. The format is as follows: 

|**Description**  |Message type and number of sensors|Name Length|Name| Length of sensor type|Sensor type|
|-----------------|----------------------------------|-----------|----|----------------------|-|
|**Size in bytes**| 1 | 1 | Name length | 1 | Length of sensor type |
|**Contents**     | First 4 bits are 0000, as 0 is the message type, next 4 bits is the number of sensors for this end node | Length of end node name | The name of the end node, where each byte is a char | Length of the sensor type | The name of the sensor type, each byte is a char |

The last two columns are repeated for each sensor on the end node.

<br />

The gateway node sends an acknowledgement containing one byte of data, the codes are as follows:

| **Ack** | **Description**                                                                   |
|---------|-----------------------------------------------------------------------------------|
| 0x00    | Successful registration; new node registered                                      |
| 0x01    | Successful registration; the sent data is the same as saved data for this node id |
| 0x02    | Failed registration; saved data for this node id differs from what was sent       |
| 0x03    | Failed registration; unknown gateway error                                        |
| 0xFE    | Bad message type received                                                         |

<br/>

**Example:** (in hex)  
Sending a registration with a name of "ITB_TEST", and two sensor types; "Turbidity", and "Temperature"

| 02 | 08 | 49 | 54 | 42 | 5f | 54 | 45 | 53 | 54 | 09 | 54 | 75 | 72 | 62 | 69 | 64 | 69 | 74 | 79 | 0b | 54 | 65 | 6d | 70 | 65 | 72 | 61 | 74 | 75 | 72 | 65 |
|-|-|-|-|-|-|-|-|-|-|-|-|-|-|-|-|-|-|-|-|-|-|-|-|-|-|-|-|-|-|-|-|

<br/>

**Rationale:**  
Sending a registration message allows the node to not have to send non changing information (like name and sensor types) multiple times, saving message space on subsequent LoRa messages. It also allows for better bookkeeping on the side of the gateway node, as it can easily keep track of which nodes are sending data to it.

<br/>

## Sensor Data

The main message sent from an end node to the gateway, contains read sensor data, time information, and gps location. The format is as follows: 

|**Description**|Message type and number of sensors|Number of Locations|Locations|Data Points|
|-|-|-|-|-|
| **Size in bytes** | 1 | 1 | 1 x Number of locations | 4 x (Number of sensors + 1) x Number of data points + 8 x Number of locations |
| **Contents** | First 4 bits are 0001, as 1 is the message type, next 4 bits is the number of sensors for this end node | Byte representing how many locations are being sent with this data | A series of bytes, each one represents the number of a data point that has an associated location | The data collected by the end node's sensors and GPS |

**NOTE:** Location data is only sent when either the latitude or longitude of the end node changes by more than 0.00005 degrees [(~5.57 m)](https://en.wikipedia.org/wiki/Decimal_degrees#Precision) due to inaccuracies possible in the gps module.

The last column is described below:

### Data points:

| **Description**   | Time | Latitude | Longitude | Sensor Data           |
|-------------------|------|----------|-----------|-----------------------|
| **Size in bytes** | 4    | 4 if it exists | 4 if it exists | 4 x Number of sensors |
| **Contents**      | An unsigned integer (32 bits) representing the unix time at which this data point was collected | A float representing the end node's latitude, nothing if this data point doesn't have a location | A float representing the end node's longitude, nothing if this data point doesn't have a location | A series of floats representing the sensor data collected for each sensor |

<br />

The gateway node sends an acknowledgement containing one byte of data, the codes are as follows:

| **Ack** | **Description**                                                                  |
|---------|----------------------------------------------------------------------------------|
| 0x00    | Success; the data was logged                                                     |
| 0x01    | Fail; this node hasn't been registered                                           |
| 0x02    | Fail; the data sent doesn't correspond to the registration data for this node id |
| 0x03    | Fail; unknown gateway error                                                      |
| 0xFE    | Bad message type received                                                        |

<br/>

**Examples:** (in hex)  
Sending one location (43.258552, -79.920548) associated with data point 1, and two data points, each with two sensor data values ((1561408970, 8.01, 17.3), (1561409031, 7.87, 17.8)):

| 12 | 01 | 01 | ca | 35 | 11 | 5d | c2 | 08 | 2d | 42 | 52 | d7 | 9f | c2 | f6 | 28 | 00 | 41 | 66 | 66 | 8a | 41 | 07 | 36 | 11 | 5D | 0a | d7 | fb | 40 | 66 | 66 | 8e | 41 |
|-|-|-|-|-|-|-|-|-|-|-|-|-|-|-|-|-|-|-|-|-|-|-|-|-|-|-|-|-|-|-|-|-|-|-|

Sending no locations and one data point with four sensor values(1561468548, 7.98, 18.2, 14, 164.8):

| 14 | 00 | 84 | 1e | 12 | 5D | 29 | 5c | ff | 40 | 9a | 99 | 91 | 41 | 00 | 00 | 60 | 41 | cd | cc | 24 | 43
|-|-|-|-|-|-|-|-|-|-|-|-|-|-|-|-|-|-|-|-|-|-|

<br/>

**Rationale:**  
The entire rationale behind this message format is to reduce overall message size on average. There is really only 2 bytes of overhead, plus one extra byte per location. The first byte of overhead can't be avoided; the message type has to be transmitted. The other bytes of overhead allow for a reduced message size, as it allows us to not send a location with every data point if it hasn't changed. This is more efficient than sending a location with every data point as long as less than 7/8 data points have a location. 

## Data Post To Server

This is the HTTP request that the gateway nodes send to the raspberry pi server to add the collected data to the database. It's in the form of an HTTPS POST request, with the following form:

POST /sensor/data?data={data} HTTPS/1.1\
Host: {Homepage}

where {data} is a long string of hex characters representing the bytes of the data collected. And, of course, this URL will vary based on what web server is being used. The byte array is in the following form:

|**Description** |Number of Nodes|Node ID|Number of Locations|Location Information|Number of Sensors|Sensor Information|Number of Data Points|Data Points|
|-|-|-|-|-|-|-|-|-|
| **Size in bytes** |1|2|1|Variable|1|Variable|1|Variable|
| **Contents** |The number of nodes that have data being posted to the server|The ID of the node who's data follows, as a 16 bit integer|The number of locations this node has to post|The location information this node is posting, empty if there are no locations to post|The number of sensors this node has|The information of this node's attached sensors, empty if there are none|The number of data points this node has to post|The data this node is posting, empty if there is no data to post|

The last 7 columns are repeated for every node that has data being posted to the server. The variable length columns are described below:

### Location Information:

|**Description** |Length of Node Name|Node Name|Data Points With Location Data|
|-|-|-|-|
| **Size in bytes** |1|Length of node name|Number of locations|
| **Contents** |The length of this node's name|This node's name, as a string of ASCII characters|An array of bytes, where each byte is the number of a data point that has location data, in ascending order|

### Sensor Information:

|**Description** |Sensor Name Length|Sensor Name|
|-|-|-|
| **Size in bytes** |1|Sensor name length|
| **Contents** |The length of this sensor's name|This sensor's name, as a string of ASCII characters|

This table is repeated for every sensor attached to the node.

### Data Points:

|**Description** |Time|Latitude|Longitude|Sensor Data|
|-|-|-|-|-|
| **Size in bytes** |4|4 or 0|4 or 0|4 * Number of Sensors|
| **Contents** |The time at which this data point was recorded|The latitude of the node at the time associated with this data points, empty if this data point doesn't have a location|The longitude of the node at the time associated with this data points, empty if this data point doesn't have a location|Data recorded by the node's sensors, represented as an array of floats, one for each sensor the node has|

This table is repeated for every data point this node is posting

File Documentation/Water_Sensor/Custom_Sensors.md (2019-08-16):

# How to Add a Custom Sensor to re:mote

This document details how to add a custom sensor to your re:mote nodes. This document assumes some Arduino (or at least C/C++) experience.

## Choose a sensor

The first step is to, of course, choose a sensor you want to add to your nodes. The sensor you choose would ideally be advertised as working with Arduino, but as long as it can be interfaced with using what's available on your micro-controller it should work.

## Interface with the sensor

Technically this step could be skipped, but it will make adding a sensor much easier. First learn how to interface with the sensor you're planning to add, then write a function that will allow the Arduino to interface with it, and test to make sure it works correctly. This is done easiest within it's own small Arduino program, as it will allow you to easily debug any issues that arise.

## Integrate the custom function with the library

To integrate your sensor with the remoteSensors library, you will need to do a few things. 

The first thing is to add a custom macro definition for your sensor. Choose a name that describes your sensor well.

The second thing, although it isn't necessary, is to add an initialisation function to the initialise() function in remoteSensors.cpp. To do this, you must add a new conditional compilation block, similar to the ones already there. Make this block check the current sensor type string against whatever string you want to name your sensor, something ery similar to the macro you defined is ideal. Within this check, call your initialisation function. Your initialisation function should do whatever needs to be done once for your sensor to work (ex: setting pin modes, configuring sensor settings, etc.).

The third, and final, thing you will need to do is add a sensor read function into the library's read() function. You will first need to add a conditional compilation block to the function, same as you did in step 2. This will block will check if the current sensor type string is the same as whatever you wish to name your sensors, once again the same as you did in step 2. Within this if statement, you will want to add the value returned by your sensor read function to the curr variable. What this does is increment the index of the data array by how much data you've added. This means that your sensor read function will have to have the following API:

* It must take as input a uint8_t representing the index of the sensor in the sensorTypes array.
* It will also take as input the pointer to a position in a uint8_t array representing the place to add the read sensor data.
* It will return a uint8_t representing the number of bytes that was written to the passed in array.

To work properly with the Gateway and server, your sensor should read and save the read values into the data array as 32 bit floats. Your sensor may read as many values as you want (ex: DHT22 reads Air_Temperature and Humidity), just be sure to add a unique string to sensorNames for every float your sensor reads. If you wish to compensate for temperature or salinity, you can add code to check for the Temperature\_Comp and Salinity\_Comp macros, and use the class variables lastTemp and lastSal as the values to compensate with. It is also important to note that if you plan on using serial communication to interface with the sensor, you must use NeoSWSerial, which only supports baud rates of 9600, 19200, 31250, and 38400.

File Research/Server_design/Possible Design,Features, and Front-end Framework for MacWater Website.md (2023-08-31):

# Possible Design, Features and Front-end Framework for MacWater Website -  Ricardo Tan
## General Design and Features 
The main goal of this website is to highlight the work that is being done by the MacWater Team. This should include information such as the general goal of the project, people involved and current work being done. The website should be able to graph the real-time data obtained from the different sensors located throughout the city.Furthermore, this website is planned to be accessible on both desktop and mobile browsers, therefore the website must be scalable for different screensizes. To ensure that our website modern, it is important to browse other websites and think about what kind of features and tools they have that could also be implemented into the MacWater webpage.

### Interactive Map 
[This interactive map] (https://cvc.ca/watershed-science/watershed-monitoring/real-time-monitoring/) by Credit Valley Conservation shows the various locations of the sensors that they have set up. When one of the locations is selected, a tag appears on top of it showing information regarding owner and type of station it is and a link to learn more about the current weather condition. The way that this can be adapted to our webpage is to have the tag showing the weather condition at the sensor location such as wind speed and ground level air temperature, then the user can click on the tag itself to be brought to a page that shows further information regarding that sensor which should include a description of the sensor and a interactive plot of the sensor's data. In the Credit Valley Conservation's map, it seems that they are using the Google Maps API, however, in our case this is not a good option. This is because Google's API has a limit on the number of times it can be accessed per day before incurring charges. Not to mention that one must sign up as a developer to get a specific API key to use, this will make a maintaining the website difficult since there are going to be different students maintaining it in the future. Currently another possible option to use is [OpenStreetMap](https://www.openstreetmap.org/), it is open-source and does not limit the number of API request in a day. However, it might not have all the functionalities that Google Maps offers.

### Interactive Plot
Credit Valley Conservation has a beautiful [plot](https://cvc.ca/watershed-science/watershed-monitoring/real-time-monitoring/west-credit-river-belfountain-conservation-area/) of their real-time data from one of their water quality station. Users can hover over data point and it will show the data's numerical value and timestamp. Another great feature of the plot is being able to adjust the time span of the data allowing more flexibility on how the user can observe the data presented. Also, users can quickly toggle between the different sensor data without having to refresh the page everytime. One interesting feature that they have is being able to have a background behind the plot, in their plots they have placed different threshold levels for the health of the aquatic life. Considering that this plot is for water monitoring level as well, all the features mentioned earlier should be included in our implementation. One minor change that could be made would be what background should be behind the plot presented. The plots that they have seems to have been licensed from [highcharts.com](https://www.highcharts.com/). While the chart looks aestically pleasing and has a lot of great functionalities, it is not open-source and has a very high cost for the licensing. One possible alternative that is open-sourced is [chart.js](https://www.chartjs.org/). Nonetheless, it is not clear whether or not it can provide all the functionalities needed.

### Export Data
This [webpage](https://ourworldindata.org/world-population-growth) is working with time-series data on world population growth provides a graph in which a csv file of the data can be downloaded by the user. This feature can be very useful because it allows the user to analyze the data further using other software of their choosing. In the webpage mentioned, the data used in the plot is static, therefore the csv file can be preassembled beforehand for the user to download. In our case, the data used for the plot is real-time, therefore user must specify the timespan of the data to be fetched from the database, then it must be converted into a csv file.

### Quick Information About Data
This [webpage](https://www.ined.fr/en/everything_about_population/graphs-maps/population_graphs/) about world population has different tools that provides general information regarding the data such as growth rate, death rate and infant mortality. A nice feature present is an interactive slider to which users can change the year of the information presented. For our uses, this can be adapted to showing information such as the minimum and maximum point of a certain sensor reading. It is not clear how they have implemented this feature specifically, but a similar function can be achieved by animating progress bars using Javascript.

### Live Newsfeed
[Toronto and Region Conservation's webpage](https://trca.ca/conservation/environmental-monitoring/surface-water-quality/) regarding surface water quality has a live twitter feed for their tweets made by them. For our uses, this can be changed to showing tweets using certain keywords. Similar feature to include would be a news feed that presents local water quality taken from a local news station website. Including a twitter feed on the webpage is simply done through their API and as for the news feed, a webscraper script is needed. 

### Scalable Top Navigation Bar (Hamburger Menu)
As mentioned before our website is planned to be used on both deskptop and mobile browser,therefore scaling of the webpage is very important. Everything on the webpage should be scalable based on the screen size, this includes text and images, and everything in between. On our website, there will most likely be a top navigation bar for users to go to different webpages. This navigation bar is usually a horizontal bar on desktop, however, on mobile it must be implemented with a "Hamburger Menu" which hides the navigation bar into one element which acts similar to a dropdown menu. An example of this can be seen on the [Government of Canada website](https://www.canada.ca/en/environment-climate-change/services/freshwater-quality-monitoring.html). Implementation of this can be done using Javascript as shown in a [tutorial by w3schools.com] (https://www.w3schools.com/howto/howto_js_topnav_responsive.asp).

## Web Design Framework
In terms of software development, a framework is a set of tools that can be used to solve a problem. In the context of web design this can be defined as a package containing standardized code to help aid the development of websites. Frameworks can be classified into one of two categories, front-end or back-end. Front-end focuses more on the aesthetics of the webpage, while back-end focuses on the logic. Front-end frameworks can be further divided into two parts which are simple and complete frameworks. Simple frameworks, divides the webpage into grids which then provides a basic layout of the possible placements of webpage elements, this framework is often simply referred to as a grid system. On the other hand, complete frameworks offer a grid system along with libraries that implement various elements such as buttons, tooltips and typography. 

### Comparison of Various Web Design Complete Frameworks

#### [Bootstrap](https://getbootstrap.com/) 
Currently the most popular framework that is used, which means that there is a lot of active communities that can act as a resource. Also, opinions of people that use Bootstrap think that it is very well documented. Bootstrap provides strong mobile support, which allows webpage to be compatible on different browsers and screen sizes. It is important to note that Bootstrap is open-source.

#### [Foundation](https://foundation.zurb.com/)
Foundation is open-source and has a mobile-first philosophy which means that developers should design how the webpage is going to look like on mobile first, then scale it up to be able to work on desktop. Furthermore, Foundation has a lot of plugins available for a more customizable development environment.

#### [Skeleton] (http://getskeleton.com/)
It is an open-source and mobile-friendly web design framework that does not have a lot of feature since the main focus is to be lightweight and responsive. What is great about Skeleton is that no compilation or installation needed.

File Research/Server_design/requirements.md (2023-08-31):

# Requirements and Existing Website Features

## Requirements

**Requirement #:** 1 <br/>
**Description:** The product shall allow manual entry of sensors' data such as its measurement type, value and timestamp <br/>
**Rationale:** To be able to enter lab samples on sensors that is currently not remotely connected to the database or captured before the system was configured<br/>

**Requirement #:** 2 <br/>
**Description:** The product shall allow pictures or videos with location tag to be stored into database <br/>
**Rationale:** Pictures or videos may provide more context regarding the data obtained from the sensors <br/>

**Requirement #:** 3<br/>
**Description:** The product shall have a map with markers of various sensors' locations<br/>
**Rationale:** There are different sensors located throughout the city, observing the location of sensors may provide more context to sensor data obtained <br/>

**Requirement #:** 4<br/>
**Description:** The markers on the map representing the sensors shall be colour coded<br/>
**Rationale:** Different types of sensors(such as pH and Dissolved Oxygen) are used, the colour provides a simple way to find the specific sensor in question<br/>

**Requirement #:** 5 <br/>
**Description:** The markers on the map representing the sensors shall have a tag popup when clicked on<br/>
**Rationale:** The tag popup will show more information regarding the sensor, including current air temperature and wind speed. Also,the tag will include a link to view more detailed information regarding the sensor such as the plot of the sensors' data<br/>

**Requirement #:** 6<br/>
**Description:** The product shall plot sensor data from database that is preconfigured<br/>
**Rationale:** The sensor will send their data to a specified database remotely, and this data should be able to be plotted<br/>

**Requirement #:** 7<br/>
**Description:** The product shall be able to set the time range on plot of sensor data. <br/>
**Rationale:** In general the plot created should have the sensor's measurement on the y-axis and time on the x-axis. Something that might be useful would be the ability to choose to look at the fine details or general trend of sensor data depending on the situation<br/>

**Requirement #:** 8 <br/>
**Description:** The product shall be able to graph multiple datasets of sensor measurement in the same plot<br/>
**Rationale:** Relationships can be found when different sensors of the same type of measurement located in different stations are graphed on the same plot.<br/>

**Requirement #:** 9 <br/>
**Description:** The plot shall show a tooltip containing the data point plotted<br/>
**Rationale:** Useful if the user wants to see the numerical value of the datapoint used in the plot<br/>

**Requirement #:** 10 <br/>
**Description:** The plot shall update as soon as the database remotely receives new data from sensor<br/>
**Rationale:** The data from sensor might want to be monitored in real-time<br/>

**Requirement #:** 11<br/>
**Description:**  The product shall show general information regarding sensor data obtained from the database,for example maximum or minimum pH value from sensor X for a specified time window<br/>
**Rationale:** Useful for quick analysis of the sensor data<br/>

**Requirement #:**  12 <br/>
**Description:** Sensor data which includes its location, measurement type, measurement value and timestamp shall be sent remotely to a specified database that is configured beforehand <br/>
**Rationale:** The database of our choosing might be more optimized for time series data, thus reducing response time when graphing the sensor data<br/>

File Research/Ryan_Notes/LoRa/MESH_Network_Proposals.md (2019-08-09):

# Overview
Three proposals will be put forth regarding possible setups for the MESH Network. The following setups are:
1. LoRa MESH Modules; modules are powered continuously
2. LoRa MESH Modules; modules synchronized to run every hour for X amount of time
3. LoRa RFM95 Modules

# Proposals 1 & 2: MESH Modules

[LoRa MESH Modules]:  
* Includes a separate processor allowing them to continue running and relaying messages while the Arduino sleeps
* Processor when Idle draws ~10mA
* Data sheets available are in a different language and fairly cryptic and there are few forums out here discussing these modules
* Modules are limited on what Parameters can be changed (SF, BW, etc) either because it is not fully understood how to, or it is not supported
* The Modules come with an SMA connector (for the antenna) already attached. This can be good for the Relayer's (it enables us to attach a more heavy duty antenna) but is an inconvenience for the Turtles Trackers (since they have to be removed; not an easy task)
* The modules may be an issue to use with the Turtle Trackers in terms of weight and size 
* The Modules handle the data relaying, so little must be done software wise other than transmitting the data

## Proposals 1: MESH Modules; continuously on
### Setup
The setup consists of three components; End-Node, Relay-Node, and a Gateway. 

End-Node - To conserve power, the MESH Modules are powered off when not used. When ready to transmit data, the modules are powered on, and data is transmitted to the desired Gateway.

Relay-Node - Due to the Modules having their own processor, the Relayer's do not require an Arduino to run. After an initial configuration, these modules simply need an antenna and battery to receive and forward data. The main issue is the large power drawn when idle. (However, the Relayer's are not limited in weight and/or size, so a larger battery and/or solar panels may be employed)

Gateway - acts just like a Relay-Node, only it will determine that it's own ID is the target ID and process the message accordingly

### Power

When idle - ~10mA
When Transmitting - ~100mA (very brief)

## Proposals 2: MESH Modules; synchronized power
### Setup

Similar to the previous setup, however, all devices are equipped with an RTC and powered off for the majority of the same. Every predetermined interval, for a predetermined window of time (both measured using the RTC), all devices will power on the MESH Modules and transmit their data. A schedule must be created so that all data is not transmitted simultaneously)

End-Node - The Tracker will power on during the predetermined time, collect, and transmit its data

Relay-Node - The Relay-Nodes require an Arduino to use the RTC with the MESH Module. The additional hardware required is compensated for with a significant decrease in power drawn from the MESH Module (since it will be powered off for the majority of the time). During the allocated on-period, the MESH module will be powered and capable of relaying any data.

Gateway - acts just like a Relay-Node, only it will determine that it's own ID is the target ID and process the message accordingly

# Proposals 3: RFM95 MESH Network
## RFM95 Background Info
See LoRa_RFM95_Module.md for Background Information

## Setup 1 - RFM95 Mesh
### Setup Outline

The setup consists of three components; End-Node, Relay-Node, and a Gateway. 

End-Node - Broadcasts a message to the Gateway, waits until an Acknowledgement is received

Relay-Node - The Relay-Node's will run through the following loop; Sleep the RFM95 & Arduino for X amount of time, run the Channel Activity Detector (CAD). If CAD returns true, break the loop. Otherwise, repeat the loop.

Gateway - acts just like a Relay-Node, only it will determine that it's own ID is the target ID and process the message accordingly

Requirements:
* The message preamble **must be greater than** the sleep time during the CAD cycle (the preamble is what the CAD looks for to see if a message is available)
* The timeout values for finding a valid route & waiting for message Acknowledgement must be changed to reflect the air time of the message and the number of nodes in the network

1. End-Node requests to send a message. A valid route must be determined. This is essentially done by broadcasting to all Relay-Nodes, and having the Relay-Nodes re-broadcast until the Gateway is found. The route to the Gateway is send back to the End-Node
2. The initial broadcast to find a route causes the Relay-Nodes to break the CAD cycle and have them wait in Receiver mode.
3. Once a route has been found, the End-Node transmits the data to the Gateway.
4. The Gateway receives the data and sends back an Acknowledgement
5. All device's go back to sleep

### Power Consumption Details

Arduino power consumption when powered -> approx. 4.5mA  
Arduino power consumption when sleeping -> approx. 72.3uA  
RFM95 power consumption when sleeping - approx. 1uA  
RFM95 power consumption when Receiving - 10 - 12mA (Depends on the settings used)  
RFM95 power consumption when Transmitting - 20 - 120mA (Depends on the settings used)  

| Mode  | Power Drawn (3V3, Arduino Pro Mini & RFM95)  | Duration (if applicable) |
|:-----:|:--------------------------------------------:|:------------------------:|
| Driver + Arduino Sleep | 72.8uA | NA |
| Arduino Awake + CAD running | Depends on Parameter values (≈5-10mA) | Depends on Parameter values (≈6ms) |
| Receiver Mode | 14.7mA | NA |
|Transmission Mode | 117mA (max value displayed) | Almost Negligible |

Note: Majority of these values depend on the what the Parameters are set to

#### Current setup value and calculations

Parameter settings and associated air time values calculated using the [LoRa Calculator][LoRa Calculator]  

Parameter Settings:  


Transmission Duration Breakdown:  


Duration and power consumed during Transmission breakdown:  


Average Current consumption for given power consumed & Duration:  


**End-Node:**  
Time waiting for an Acknowledgement
* Greater than the time to send a message to the Gateway and send a message back

**Relay-Node:**  
Time between running CAD
* Depends; longer time equals less power consumed in the long run, but it requires the message preamble to be longer; causing all messages to take longer to send
* 500MS seems like a good choice
* Don't try to have Arduino sleep while CAD runs. Interrupts are handled internally by the RadioHead Library and trying to use the interrupt messes it up (plus CAD runs quick enough that having the Arduino sleep isn't really needed)

Time spent waiting for the actual data to transmit?
* Must be long enough so that a route may be found, the data transmitted, and an Acknowledgement received

**Gateway:**  
Identical to Node, only the data will be processed upon realizing it's ID matches that of the target ID for the data; processes the data accordingly

## Setup 2 Outline - RFM95 Flooding
### Setup Outline

The End-Node broadcasts its message, and all Relayer's within range rebroadcast the message. Eventually, the message will be received by the Gateway.
The Gateway then sends an ACK back. Precautions are taken to avoid broadcast storms and discard stale messages.

Message Format - [ACK]|[Lifespan]|[Message ID]|[Message Data]  
ACK - 0 or 1 ( 0 = not an ACK, 1 = is an ACK)  
Lifespan - Exceeding a threshold will result in the message being terminated  
Message ID - Uniquely determined using the Node ID, # of nodes in the network, and the # of messages the node has sent  
Message Data - Reason for the message transmission. This data could be GPS coordinates, commands, etc.  

End-Node - Constructs and broadcast the message. Enters the CAD loop and, when a message is detected, checks if it matched the assigned message ID of the message it sent, and whether it is the acknowledgement or not

Relay-Node - Stays in the CAD loop until a message is detected. When a message is received, the below condition table outlines the steps taken to determine whether to relay the data or not. Afterwards, the Relayer re-enters the CAD loop  



* If seen before, should not relay!

Gateway -  Stays in the CAD loop until a message is detected. When a message is received, it checks whether it has already seen the message. If not, it saves the message ID, resets the Lifespan count, Sets the ACK TO 1, and broadcasts the message

* Main issue is message collisions. [This][LoRa Scalability: A Simulation Model Based on Interference Measurements] paper has some interesting notes regarding message collision between LoRa Modules
## Other Potential Setup Ideas (some are repeats of above)

* Currently have the Relay-Nodes and Gateway break the CAD cycle and run in receiver mode for a set amount of time. Instead, have them break the CAD cycle, process the message, then re-enter the CAD cycle. Whether it's a broadcast to find a route, the actual data being sent, or the Acknowledgement; as long as the preamble is set long enough, the Relay-Nodes & Gateway should have enough time to exit the loop and receive the message.

* Ignore the MESH Network Protocol completely. Instead, just have the End-Node Broadcast its message to all Relay-Nodes. They will then rebroadcast the message until it makes it to the Gateway. The Gateway will then do the same thing for the Acknowledgement. This is known as **[Flooding][Flooding]**
	* Ensure each node only relays a message once. Perhaps create a circular array that stores an ID for the message. Circular so that the oldest message (that has most likely expired long a go), is removed
	* Each time a message is relayed, increment a counter (that is a part of the message) by 1. Once that message exceeds a value, do not re-transmit it
	* If a node has already received the ACK for a message it is suppose to re-transmit, do not re-transmit the message
	* Potential issue with multiple Gateways receiving the same message	

* End-Nodes broadcast the message, but Relayer’s have a specific, predetermined route (similar to what Emil mentioned in his email)
	* Issue of a node fails (cuts off connection for that "branch")

* **Basic MESH Netwrok setup, but collect data for the day and send in one go (data dump).**

* MESH network flow
	* Sends broadcast to find route, broadcast is received and forwarded until it reaches the Gateway. The final route is forwarded back. (I think) Each broadcast should have the same air time and preamble length (data sent by gateway may be longer since it sends the routing table)

[LoRa MESH Modules]: https://www.dfrobot.com/product-1670.html

[LoRa Calculator]:https://www.loratools.nl/#/airtime

[Phase, duration, and power consumed]:https://i.ibb.co/7tL8Mkz/Phase-duration-and-power-consumed.png
[Setup Runtime]:https://i.ibb.co/XSy0sHY/Setup-Runtime.png
[Current Calculations]: https://i.ibb.co/hMd9f9M/Current-Calculations.png
[Parameter Settings]: https://i.ibb.co/hHT9zHZ/Parameter-Settings.png

[Flooding]:https://en.wikipedia.org/wiki/Flooding_(computer_networking)
[Flooding Relay Condition Table]:https://i.ibb.co/QDZJ7xx/Flooding-Relay-Condition-Table.png

[LoRa Scalability: A Simulation Model Based on Interference Measurements]: https://www.mdpi.com/1424-8220/17/6/1193

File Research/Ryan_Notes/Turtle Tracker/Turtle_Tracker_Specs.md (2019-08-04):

# Overview
* Hardware Specs
	* Battery
	* GPS
	* Micro-controller
	* Casing
* Pinout
* Waterproofing methods
	* 3D Printing

# Hardware Specs
## Lithium Ion Battery - 400mAh
### Dimensions
[Dimensions][Battery Dimensions Source]: 26.5mm x 36.9mm x 5mm  
[Weight][Battery Weight Source]: 9g
Order: https://lowpowerlab.com/shop/product/145




## GPS - GP-735
### Dimensions

[Dimensions][GPS Dimension Source]: 8(W) x 35(L) x 5.2(H) (mm)  
[Weight][GPS Weight Source]: 4.3091275 g (0.1520 oz)




* When EN pin is LOW, RTC is not retained. Must use the V_bAT pin
* EN Pin and V_BAT Pin work as expected
	* Haveing V_BAT Pin powered while EN Pin is LOW (i.e. GPS is at full power) does not cause excess current drawn. So the V_BAT pin can be left HIGH indefinitely (may require additional tests to confirm)
* B_BAT Pin output HIGh when Arduino In Low Power?
	* yes
* GPS needs full Position data before it saves the RTC and position. After that, Enable and Backup work as expected

### Power Consumed

Voltage - 3V3 & 5V(Voltage Regulator Used)
* On - 42-47mA
* Off - 32.9uA
* Battery Backup - ?

### Average Fix Times

Cold start (no RTC)
Warm start (RTC) - 

## Micro-controller + LoRa
### Dimensions
[Dimensions][Board Dimension Source]: 22.86 (W) x 50.8 (L) x 1.6 (H) (mm) (2 x 0.9 inch) (Height from CAD File)  
[Weight][Board Weight Source]: ???

Specs for the board can be found [here][Board Specs]. The specs are in the form of a CAD file.

### Power Consumed
* rfm95 put to sleep for these tests (i.e. negligible current drawn by it)

Voltage - 3V3 (Voltage Regulator Used)
* Idle (Empty setup + Loop) - 6.67mA
* Low Power - ~8.0uA

Voltage - 5V (Voltage Regulator NOT Used)
* Idle (Empty setup + Loop) - 5.32mA
* Low Power - ~1.324uA

## Pinout

Moteino | RFM95
D2 -> Interupt  
D8 -> Reset (?)  
D9 -> LED  
D10 -> Slave (?)  
D11 - D13 -> SPI  

Moteino | GPS  

D3 -> RX  
D4 -> TX  
3V3 -> VCC  
GND -> GND  
5 -> EN  
6 -> B_Bat  

Moteino | Battery  

Vin -> VCC  
GND -> GND  

## Casing

* CAD design made up of 4-pieces - 2 end pieces, bottom & top piece
	* Bottom has a slight curve on the bottom, flat ends, narrow. The curve can be altered based on the turtles shell. It's mostly solid except for a hollow rectangular shape on the inside where the battery will fit into. One end is slightly longer and flatter for the Boards antenna to lay.
	* End pieces are customized based on the turtles shell. 
	* Top piece is more of a shell then a case. It covers the board and GPS. The top is non-existent, allowing the GPS to be uncovered. It has a slight curved shape 
		* If needed, the top case can be cut away slighlty to expose the LoRa antenna. This can be done if the casing blocks the signal (although it'll make the casing less streamlined) 

The below images show an exploded view of the Tracker and casing. From top to bottom; Casing - top, GPS, Moteino board, Battery, Casing - Bottom










# Waterproofing Methods

*  In these cases you should consider post processing your print to seal the surface. The **ABS smoothing technique with acetone** could do this, or you could add an **epoxy mix like XTC-3D to smooth and seal the surface**. Finally, there are a number of **conventional sealants one could use, including paint**. [1]

* Plastic Spray paint
* Conformal coating
* Painting the print with epoxy

* acetone works only with ABS

* Attaching the top and bottom case
	* Glue
	* 4 pins on each corner of the top case that clip into the botoom case. How to unclip though?

## 3D Printing

* Materials available - PLA (Makerspace & Mills)
	* tend to soften and eventually dissolve if exposed to water for any length of time. [1]

[Battery Dimensions Source]: https://www.sparkfun.com/products/13851
[Battery Weight Source]: https://www.canadarobotix.com/products/940?variant=14423573397553
[Battery Image]: https://i.ibb.co/bWXy8mQ/Battery-Image.jpg
[Battery Specs]: https://i.ibb.co/8M1JmK7/Battery-Specs.png

[GPS Dimension Source]: https://www.sparkfun.com/products/13670
[GPS Weight Source]: https://www.amazon.com/GPS-Modules-Receiver-Channel-GPS-13670/dp/B07QC5HL1D
[GPS Image]: https://i.ibb.co/TtLrFxD/GPS-Image.png
[GPS Specs]: https://i.ibb.co/7NC8dyF/GPS-Dimensions.png

[Board Dimension Source]: https://lowpowerlab.com/shop/product/145
[Board Image]: https://i.ibb.co/sg7LxYL/Moteino-Board-with-Trace-Antenna.png
[Board Specs]: https://lowpowerlab.com/guide/moteino/design-files/

[View1]:https://i.ibb.co/RcnK4N8/View1.png
[View2]:https://i.ibb.co/mXG7mpS/View2.png
[View3]:https://i.ibb.co/89PmXMY/View3.png
[View4]:https://i.ibb.co/mBGmSBq/View4.png
[View5]:https://i.ibb.co/8xTZkHZ/View5.png
[View6]:https://i.ibb.co/10kK3cs/View6.png
[View7]:https://i.ibb.co/5s4s3Yg/View7.png
[View8]:https://i.ibb.co/RBQY0Yx/View8.png

[Vapor Polishing ABS 3D Printer Filament]: https://www.matterhackers.com/articles/how-to-vapor-polishing
[Mouldable Glue]: https://sugru.com/about

[1]: https://www.fabbaloo.com/blog/2017/10/19/waterproofing-your-3d-prints

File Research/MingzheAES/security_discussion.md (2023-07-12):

## Differences between Lora and LoraWan
 - Lora: https://forum.arduino.cc/t/lora-encryption/587754 
    - Data consists simply of a collection of bytes. The radio does not know or care whether the collection being sent is encrypted.
    - There are many different encryption libraries for Arduino. (Just pick one, learn how to use it, and encrypt the data buffer before sending it by radio. Decrypt at the other end.)
    - Encryption library document: https://rweather.github.io/arduinolibs/crypto.html 
    - Encryption library src: https://github.com/rweather/arduinolibs 
 - LoraWan: 
    - Architecture: https://lora-alliance.org/about-lorawan/ 
    - Security implementation (AES 128 bits): https://lora-alliance.org/resource_hub/lorawan-is-secure-but-implementation-matters/

## Security requirements:
 1. No one can receive our data (if received, cannot decrypt)
    - Solution: any encryption (either symmetric or asymmetric) solves this problem
 2. If someone physically gets the tracker, they will get the key stored in the tracker, therefore we should not store the key (plaintext) in the tracker 
    - Candidate solution: no good solution for now, but it's a little impossible that someone could get a tracker and try to decode it.
 3. No one can send us faked data 
    - This issue only exists when the asymmetric algorithm is selected
    - Candidate solution: use serials number to distinguish unique hardware (e.g. by using some hardware id that are globally identified)
    - Note: currently, the `id` is hard coded in the source code (different source codes) 

## Analysis
 - AES is symmetric encryption. LoranWan officially uses AES 128 bits to secure Lora physical layer.
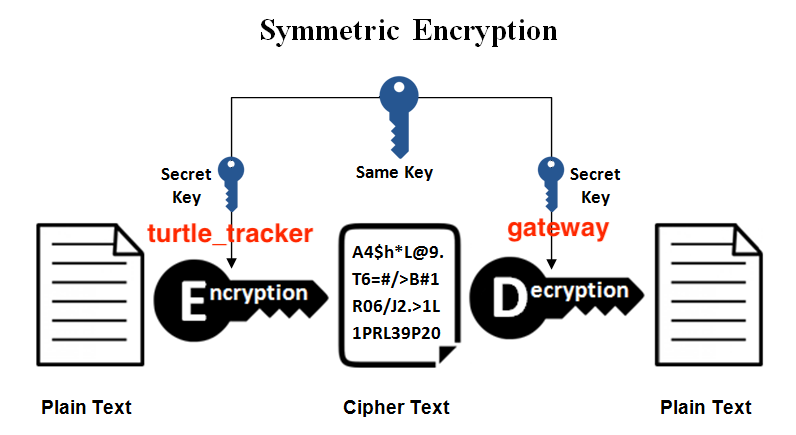
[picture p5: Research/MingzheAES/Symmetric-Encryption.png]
 -   
 (src: https://www.ssl2buy.com/wiki/symmetric-vs-asymmetric-encryption-what-are-differences)
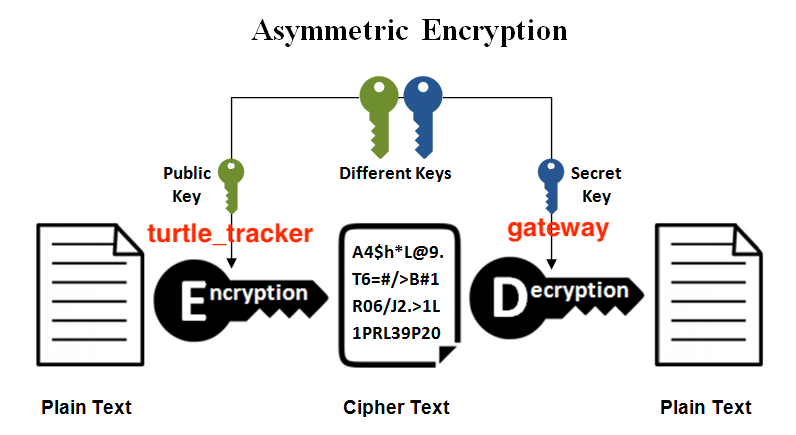
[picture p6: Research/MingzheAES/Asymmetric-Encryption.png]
 -   
 (src: https://www.ssl2buy.com/wiki/symmetric-vs-asymmetric-encryption-what-are-differences)
 - The main constrains of selecting an encryption method should be the **energy cost** and **memory usage** in the encryption stage (where both the battery and memory is limited), so we need an algorithm that makes sure the above 3 security requirements with the least time and space comlexity.

## Unfinished tasks: 
 - Check if some components of Moteino (the board using LoRa) has a unique MAC address/encryption module. (e.g. the GPS module has a unique id?)
 - Check if there's some implementation of Diffie–Hellman in Arduino.
 - Moteino datasheet:  
 https://ww1.microchip.com/downloads/en/DeviceDoc/Atmel-7810-Automotive-Microcontrollers-ATmega328P_Datasheet.pdf 

## Dr. Jelle's suggestions: 
 - For turtle trackers, we don't care if someone sees the history of a tracker, so symmetric.
 - For water sensor: we want long-term privacy, so asymmetric.
 - Diffie–Hellman in Arduino (search in Google)
 - SSL in C: https://bearssl.org/

## Useful implementation hints:
 - Diffie–Hellman for bi-direction communication between tracker and gateway.
    - tracker -> gateway: to send the data 
    - gateway -> tracker: to see if the tracker is still alive, remotely configure the setting
 - A helpful article about security in Arduino: https://blog.arduino.cc/2020/07/02/arduino-security-primer/

## Current chosen solution
- Tturtle trackers: automatically generate the key (Diffie–Hellman), and then combine that key with AES 128 to finish the encryption.
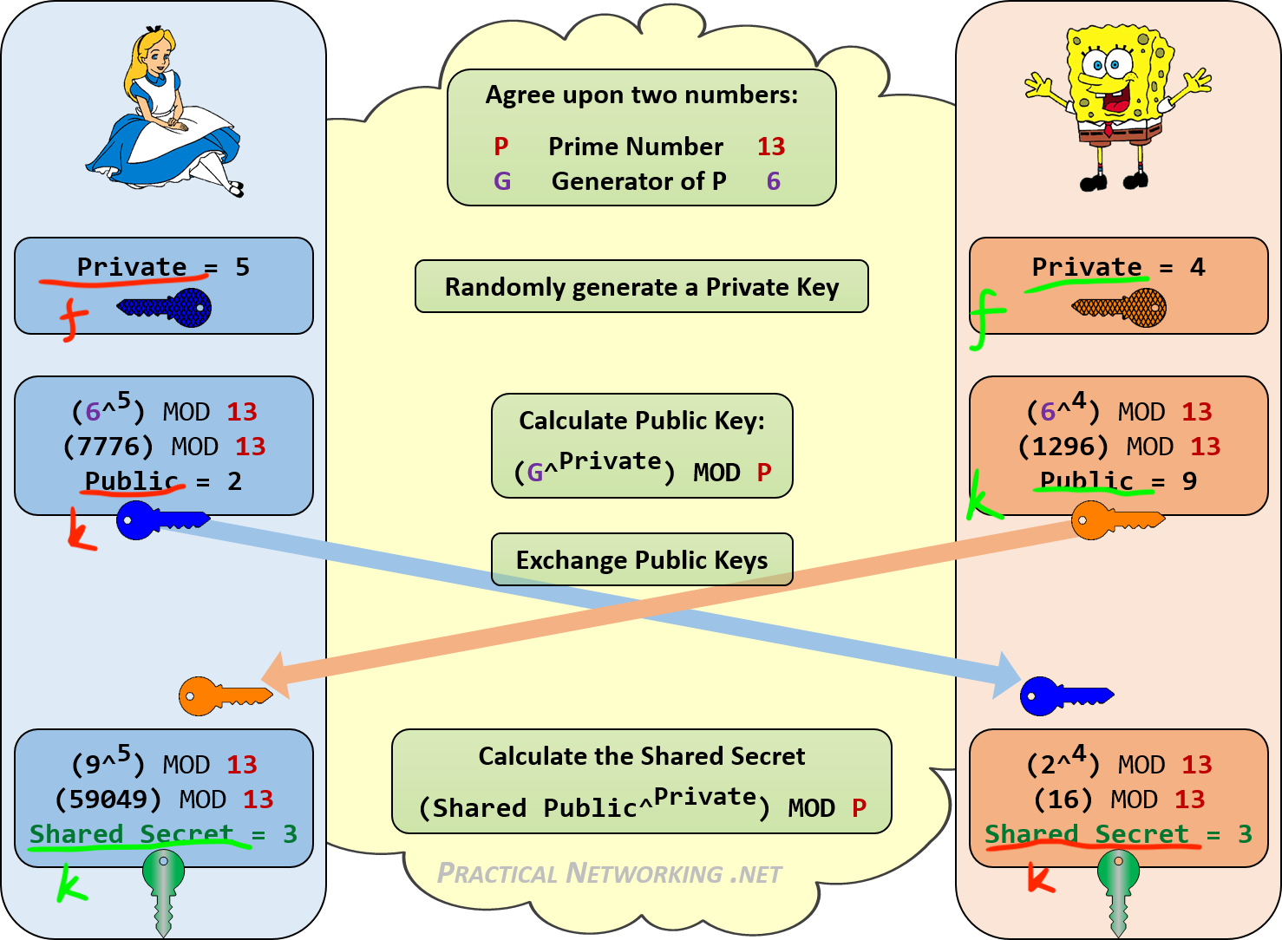
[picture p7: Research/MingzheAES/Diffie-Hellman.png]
Diffie-Hellman
  -   
  (src: https://www.practicalnetworking.net/series/cryptography/diffie-hellman/)
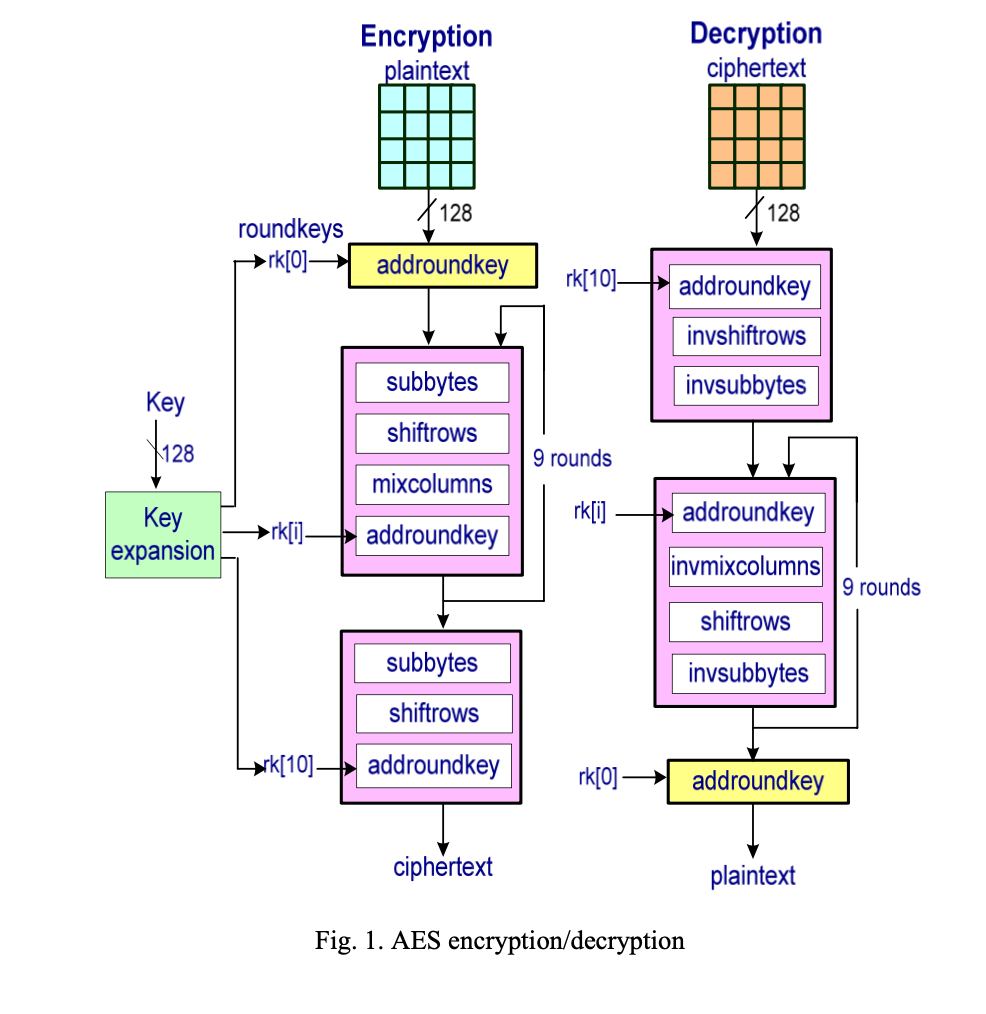
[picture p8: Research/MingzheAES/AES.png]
AES 128
  -   
  (src: https://www.researchgate.net/figure/llustrates-the-encryption-decryption-rounds-of-the-AES-128-The-cipher-maintains-an_fig1_274027061)
 - Water sensor: to avoid the gateway storage to be hacked, an asymmetric algorithm must be used. (e.g. by using the `SSL` library in C)

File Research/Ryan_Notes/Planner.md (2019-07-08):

# Meeting/ToDO
1. What I've been doing for the past 3 days
    * Reading about the LoRa rfm95 modules and what they are capable of
        * Much like the GPS's, these modules are packed with features, went through very slowly to learn about a lot of them
    * Reading forums to see what people have done
        * Wanted to see what was out there in regards to a low power listening mode
2. Show the notes I took while reading
3. Outline what I've come up with experimentally, the benefits, and how it could be applied to our projects

* Recorder EVERYTHIND read/attempted/done
# TODO List (In order of Priority)

1. Make up a doc about all the different components/sensors used (LoRa, arduino's, etc), write down the power consumed, whats good about it, why we didn't use it etc.
    * LoRa Modules
    * Different Microcontrollers
        * Arduino
        * Motenio
        * Texas Intruments

2. Make up 3 different tests for potential MESH setups
    * MESH modules; always running
    * MESH modules; synchronized using RTC to run 10min every hour
    * RFM95 Modules; Need more research

3. Unify Code between projects and get on the same page for the different setups (Trackers, nodes, Gateway, relyers)

4. See if Can put GPS into sleep mode (i.e. use Enable Pin) via commands using U-center

5. Use rfm95 with turtles and MESH for other stuff. MESH has the SMA connector already on, good for relayer's, bad for trutles (it'll have to be removed)

1. Solder pins on water sensor
7. Check range of RFM95 Modules

3. Use GPS signal for testing underwater; have LoRa transmission as a backup (since packets may be lost, not reliable method)

4. Check out the Datasheet of the LoRa MESH Modules provided by Spencer

3. Try RTC test again, this time let GPS run for 20sec every hour
    * Just have a check for if any satellites have been acquired in X amount of time 

4. Brainstorm ideas on how to locate the turtle
    * What if the Tracker battery dies?
    * Arduino is completely powered off. How are you suppose to locate it?
    * MESH module from 10ma in IDLE so it cannot be left on. How about the other LoRa modules in IDLE? If they don't draw a lot pf power, they can be left on, and maybe used as an interrupt.
9. Issues with MESH modules conflicting issue. Try using Victors Acknowledgement code?
2. Put together an order list for the Turtle Trackers
5.
6. See if a MESH network with the RFM95 modules is possible and power consumer is low

# Ideas for the Above Stuff
* Locate Turtle
    * Have a check for battery voltage. When it drops below a certain level, an alternate mode is activated. For example, the Tracker becomes a beacon, outputting it's GPS coordinates every 10min or so (assuming it is not underwater). The payloads in this mode could be marked differently so it is know that the Trackers have entered a low battery state.
        * The LoRa rfm95 modules apperently have a Low Battery Indicator that is set when the voltage goes below a certain threshold

* The rfm95
    * Can be put to sleep (draw about 20 uC)
    * Apparently has a Low Battery Detector and Temp. Sensor

* Always have the Trackers able to receive
    * The rfm95 modules have a mode called Channel Activity Detection (CAD). This mode basically checks to see if there are any messages in the air. This mode runs for a very short period of time (it is based on the SF and bandwidth) and draws little current. The Trackers can be put in a loop where every X amount of time (500ms, 4 seconds, etc.), the Arduino wakes up, enters CAD mode, if it returns false, put the driver to sleep and then the Arduino to sleep. If it returns true, that means a message is in the air, turn on and wait to receive.
    * Still working on getting it to run smoothly but
        * Looks like current consumption is still very low. Will try connecting to Arduino Pro Mini and see what overall consumption is.
        * Whatever is sending the message must do so multiple times. the first message will be to wake the Tracker up, than it must be sent again for the Tracker to receive it. The Radiohead library already conmes equiped with the abilty to continuously resend unreceived messages so not a big deal
        * In regards to a MESH network, have not tried yet. A library already exists to create one. I believe, if I can get the packets sending/receive smoothly without anything being missed, I could get this working.

* The Trackers are not configurable, but the Gateways are, and they can communicate with the nodes
    * When data is sent from the node to the Gateway, the Gateway can send back the ACk along with some commands on what the Node should do, such as enter Beacon Mode for locating.

* With the RFM95, try,
    * Setting up a Mesh network
    * Low power, always receiving mode?
    * Wake up Arduino via Interupt pin?

* To prevent Arduino from running while CAD is on (CAD runs for very short period of time, but Arduino will still draw decent current in that time)
* Arduion wakes up, runs cad (does it block?)
* Attach interrupt to pin that CAD outputs to
* Have Arduino sleep until woken by CAD
* Proceed normally

# Meeting Outline

1. Configuring GPS via Arduino
    * Sending commands is easy. Just copy Binary commands produced by U-center and paste into Arduino code. Easy to add more commands
    * Reading also farily easy, somewhat tedious to organize what's been read. Not very beneficial for Trackers. More useful for Gateways
    * List of useful data to read from GPS
2. Go over current Tracker code
    * Disucss RTC algorithm
    * Discuss GPS algorithm
3. What to focus on at the moment?
    * continue making Tracker code, keeping it as generic as possible with code dependent on the hardware being used

# Future Plans

* Create a breakdown for the Trackers
* Create new test procedure for LoRa Range

* Look at which ephemeris data has been downloaed for each sateliites
* Use Watchdog timer to sleep during specific time - get GPS time when available to self-correct
* Look through UBX protocol to see what data can be read from GPS
* Use the LoRa Module to check if Tracker is underwater. If no acknowledgment is recieved, GPS is underwater
    * Issues - Gateway breaks at some point, Gateway is out of range
    * Pros - Much cheaper on power

* Watchdog accuracy test
    * Done see notes and data
* RTC on GPS?
    * Yes. See notes
* Read RTC without fix (and if it's reliable)
    * Yes. See Notes

* Look at different GPS modules 
* antennas (what would be good for our application)
    * Look into the various parameters to change (size, shape, type)
    * Not to detailed. Look around, see what people have used
* Bounce back to LoRa every so often

* Send/recieve messages using UBX via the Arduino

# Meeting Outline & Notes
1) Go over GPS Notes again, going over the sections that have been added and given in more detail
    * How to guage the GPS accuracy (PDOP)
    * Improving GPS Accuracy (DGNSS, SBAS)
    * Almanac Data, Ephemeris data, trasnmission of this data
    * Start-up modes and their requirments
2) Show U-Center Notes
3) Testing Notes
    * Power Saving Mode doesn't seem to be appropriate for the Turtle Trackers. This mode is geard towards GPS's that will always remaine powered on and require position fixes relativley frequently.  
For our application the idea is to get a fix as quickly as possible, record the position, than cut all power to the GPS. The usefulness of PSM occurs after the GPS has aquired it's fix, and it is at this point that all power is cut to the GPS anyway's.   Therefore, it makes no difference to have the GPS run in Continuous mode or Power Saving Mode.
4) Thoughts and Ideas (below)

# OverView and Plan:

* Overall Goal - Reduce how long the GPS's are ON to minimize current drawn and maximize battery life
* How to acheive this - Provide the GPS with data that will aid in aquiring a quicker fix.
    * Almanac Data - Have GPS run for 12.5 min initially to download all data. Data will be useable for entire duration of project
    * Other data - DYnamically downloaded while deployed
* How is this data provided
    * Data is stored on the GPS's BBR
    * Data is transmitted to the GPS's via the Gateway's
* How long should the GPS run for?
    * Run time should be dynamically chosen based on the following
        * Type of Start (Cold, Warm, Hot)
        * Time since last fix (i.e. time underwater)
        * Potentially - Cloudy/clear conditions?
    * Run time will influence,
        * ephemeric data downloaded
        * Aided data downloaded (Assit Autonomous)

## Additional Ideas:
* **Could have the Gateway transmit the ephemeris data to the Turtle Trackers to minimize the time the trackers remain on**
* **Use the Gateways as a Base Station**

## Extra Notes:
* GPS must initially run for approx. 12.5min to aquire all Almanac data. The more the better. Acquiring it from all satellites would be ideal

* Time underwater is propotional to the additional amount of time the logger can spend to get a fix
    * If the Tracker is underwater, it won't turn on to get a fix. For everytime this occurs, the Tracker is allowed to spend that much longer getting a fix once it surfaces without taking a loss on battery life
    * Have a counter. If Tracker  does not acquire a fix after x counts (each count representing time it should have gotten a fix but didn't because it was underwater), increase the time the Tracker stays on when it can get a fix

* **Many of these Assisting features are extremely challenging to test. It's very difficult to determine not only if the aids are being used, but if they've made any noticable difference. Their effectiveness also fluctuates with the position of the satellites**
    * If the Trackers and Gateways are in sync, can have the Gateways braodcast relevant data for the Trackers to use

* I think Assist Autonomous starts running after it has downloaded the ephemeris data from a satellite. Look at how long it takes to download the data to get an idea of total time to completion

* **Use of an RTC will be useful for the following reasons,**
    * Provides accurate time to the GPS
    * Allow us ti implement a secific time interval for the GPS Trackers, which can increase the battery life

## Potential Plan A:
* The original GPS's data not stored data for future use, resulting in them always running a Cold Start. The addition of a BBR is the major change to the GPS's (minor changes include altering the configuration sttings via U-center)
* In scenario's that the turtles is out of the water, and the GPS is capable of getting a fix every hour, with the aid of the BBR, a fix can be obtained in < 30sec.
    * If time is givene to allow ephemeric data to be downloaded, this can be reduced to approx. 1sec (problem is knowing how long to leave the GPS on for to download this data)

* Have a minimum time that the GPS will ALWAYS stay on for.
    * Around 30sec should be good. 
        * If it already has ephemeric data, it will get a fix quickly, and provide enough time to download more data
            * Time can be cut down for this scenario
        * If it is starting from a Warm Start, 30sec should be good for a fix only
        * From a cold start, use the underwater counter to add additional time accordingly

## Potential Plan B
* The best option may be to configure everything via U-center, and stick to recieving NMEA messages via Arduino. You can't really monitor when or if Assist Autonomous has done anything. Same goes for downloading Ephemeris and Alamanc data. Maybe every so often, let the GPS run a bit longer after getting a fix to get some ephemeris data (but that may just be a waste of time since it won't be valid for very long)
    * Can save the confiuration options and quickly load it onto the GPS via U-center. Could probs do via Arduino (just load and send the text file)

# Other
* Let the other GPS module run for a while and record the log. Do that again tomorrow and comapre the data (and see if the data even saved overnight)
* Both the original and the NEO-6M GPS's **DID NOT** save the data (at least not long enough to be useful). After 16 hours, the set configuration and almanac data was gone)
    * 1 hour intervals may be okay

* **100% confirmed - The Original GPS's do not have memory to store the config. or other data**

* Use noise/jammer/combo of 2 to check the following
    * Underwater and won't get a fix
    * Above water but very cloudy - fix unlikley
    * Above water and clear skies - easy fix

Hardware Configuration:
===

* Configuration data, Almanac data, ephemeris data, and Assist Autonomous data will be saved to the BBR (Battery Backed RAM)
*  GPS's most recent position, time, etc. are automatically saved to the BBR

* The battery is **suppose to** automatically recharges when the unit is powered and has a lifespan of approx. 2 weeks (the Arduino will still peridocially be waking up so the battery should always have a charge)
    * May need an RTC for this data to be useful

* Using the SPI pins, the GPS can utilise the Arduinos EEPROM. This can be used to store Assist Offline Data and the GPS's most recent position
    * Using this data requires a **RTC**
    * It will garuentee a fast TTFF for **at least** the first 14 days of operation
    * "u-blox provides correction data valid from **1 to 35 days**. The size of these files increases with the length of the prediction period, from as little as **3 kB to 125 kB**. Positioning accuracy decreases with the length of the correction data duration, with 1–3 day data providing relatively high accuracy and 10–35 day data progressively less accuracy."

Software Configuration:
===

Algorithm:
---
* Needs to know:
    * When to aquire new ephemeris data
    * When ephemeris data has expired
    * When Jamming is occuring
    * When to perform Autonomous calculations
    * How much time to provide for getting a fix, performing calculations, and aquireing new data
    * When it is safe to power the GPS off
 
* Combo of Downloaded data and AssitAutonomous (in case memory is an issue)
    * Download data 3 days apart. Use AssistAutonomous to determine data within those time blocks

## Questions
* how long does it take to get Autonomous data? Can computations be done while the GPS is in a Low Power Mode? What requirements must be met before Autonomous can do its calculations?

* How does the GPS know when the saved data is no longer valid? (it would need a clock)
    * Note that the receiver requires an **approximate value of the absolute time** to calculate AssistNow Autonomous orbits. For best performance it is, therefore, recommended to supply this information to the receiver using the UBX-AID-INI message in a scenario without a running RTC (i.e. without backup battery).

[1]: https://www.measurementsystems.co.uk/docs/TTFFstartup.pdf

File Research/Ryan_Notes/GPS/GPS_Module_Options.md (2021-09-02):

* Price range?
* Probably better off buying a pre-made board rather than design our own PCB. A lot of things that need to be considered when designing your own board
 * Include key, important feature relevant to the project, and provide a link to the datasheets

 # What we're looking for
* Cheap
    * < $50
* Capable of backing up RTC and aided data
* Various mode of operation for altering power consumption
* Configurable
* Low Current consumption
    * < 50mA
* Quick fix
    * < 30 sec

 # [GPS Receiver - GP-20U7][GPS Receiver - GP-20U7 Specs]:

* Dimensions: 18.4mm x 18.4mm x 4mm
* Weight:  

 * 56-Channel Receiver (22 Channel All-in-View)
 * Sensitivity : -162dBm
 * 2.5m Positional Accuracy
 * Cold Start : 29s (Open Sky)
 * 40mA @ 3.3V

* Does contain a RX header so that commands can be sent to it (although it's been covered by tape and a ire would need to be soldered to it)
* Despite having a battery, it does not appear as though config or aided data is saved.

# NEO-6M GPS Chip:

* Dimensions: 28mm x 28mm x 8.6mm
* Weight:
    * Chip: 
    * Board:

* [NEO-6M GPS Chip][NEO-6M GPS Chip]
* [NEO-6M GPS Board][NEO-6M GPS Board]



This GPS module continues to appear as an excellent choice for low-power, low-cost projects. A few of the key features are:

* _Power Save Mode(PSM)_: It allows a reduction in system power consumption by selectively switching parts of the receiver ON and OFF. This dramatically reduces power consumption of the module to **just 11mA** making it suitable for power sensitive applications like GPS wristwatch [[4]]

* The breakout board include a battery and EEPROM for memory storage. Utilizing these retains clock and last position, causing **time to first fix (TTFF) to reduce to 1s**.[[3]]
    * Without the battery the GPS always cold-start so the initial GPS lock takes more time [[3]]
    * The battery is automatically charged when power is applied and maintains data for up to **two weeks without power.** [[3]]
        * **Battery is not a reliable source. Too many unknowns, such as lifespan, recharge time, etc.**

* Both modules support UBX and so are compatible with **U-center from u-blox** for evaluation, performance analysis and configuration of u-blox GPS receivers including NEO-6M

* The EEPROM on the Board communicates with the NEO-6M chip using I2C
* To save data (such as Assit Offline) an external memory (Flash) must be connected to the chips SPI header.
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

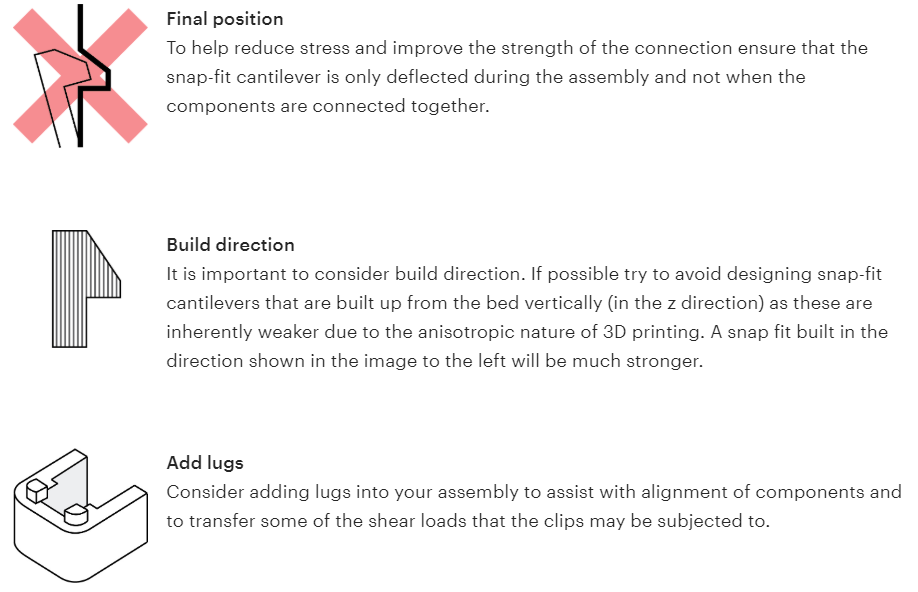
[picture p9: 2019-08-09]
Research/Ryan_Notes/Images/Joints/Good Design Practice-2.PNG

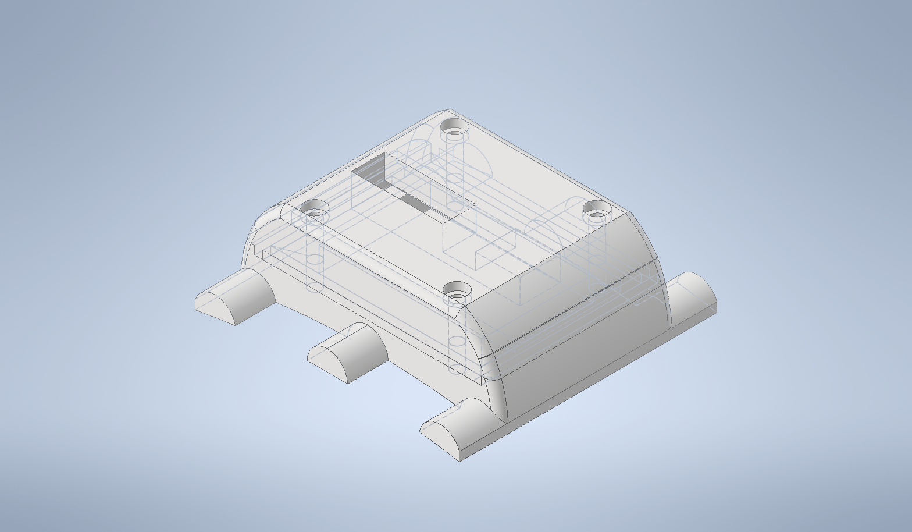
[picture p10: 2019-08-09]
Research/Ryan_Notes/Turtle Tracker/Enclosure/Enclosure Designs/Tracker V4/Pictures/View1 (1).png

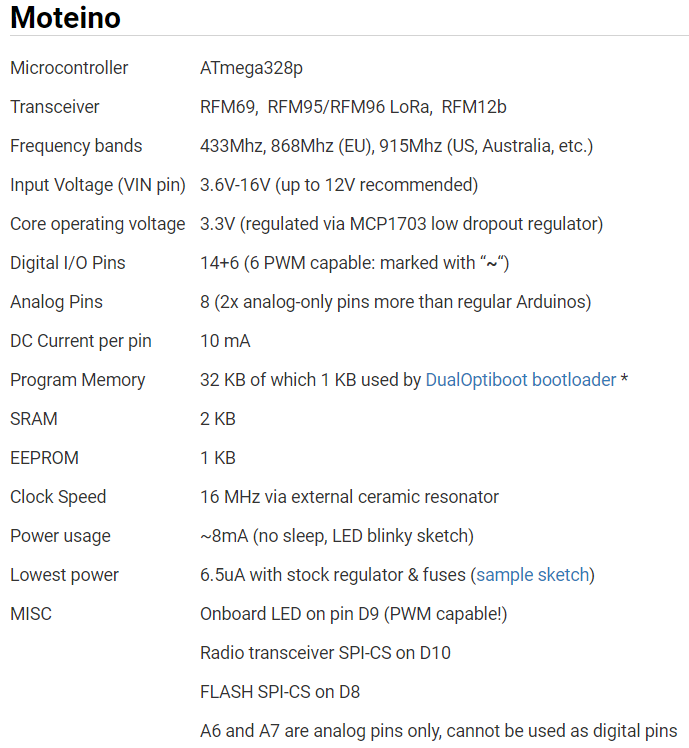
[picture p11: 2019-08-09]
Research/Ryan_Notes/Images/Moteino/Moteino Specs.PNG

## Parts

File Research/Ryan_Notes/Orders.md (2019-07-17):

Item: FTDI Adapter
Date of Order: April 30
Link to Site: https://www.amazon.ca/gp/product/B07BBPX8B8/ref=ppx_yo_dt_b_asin_title_o00_s00?ie=UTF8&psc=1
Comments: NA

Item: 2 x NEO-6M GPS
Date of Order: May 24
Link to Site: https://www.amazon.ca/gp/product/B073MFYL8B/ref=ppx_yo_dt_b_asin_title_o02_s00?ie=UTF8&psc=1
Comments: Had to return 1 of the modules due to a defect

Item: Micro SD Card Adapter
Date of Order: May 24
Link to Site: https://www.amazon.ca/gp/product/B07GXBP672/ref=ppx_yo_dt_b_asin_title_o01_s00?ie=UTF8&psc=1
Comments: NA

Item: Miini Display Port Adapter
Date of Order: 
Link to Site: https://www.amazon.ca/gp/product/B01N4M65D7/ref=ppx_yo_dt_b_asin_title_o01_s01?ie=UTF8&psc=1
Comments:

Item: 4 x GPS Receiver - GP-735
Date of Order: July 16/17, 2019
Link to Site: https://www.digikey.ca/product-detail/en/sparkfun-electronics/GPS-13670/1568-1467-ND/6578384
Comments: NA

Item: 5 x JST SH JUMPER 6 WIRE ASSEMBLY
Date of Order: July 17, 2019
Link to Site: https://www.digikey.ca/product-detail/en/sparkfun-electronics/PRT-10361/1568-1500-ND/6605206
Comments: NA

Item: 2 x Moteino (Trace Antenna)
Date of Order: July 16, 2019
Link to Site: https://lowpowerlab.com/shop/product/145
Comments: NA

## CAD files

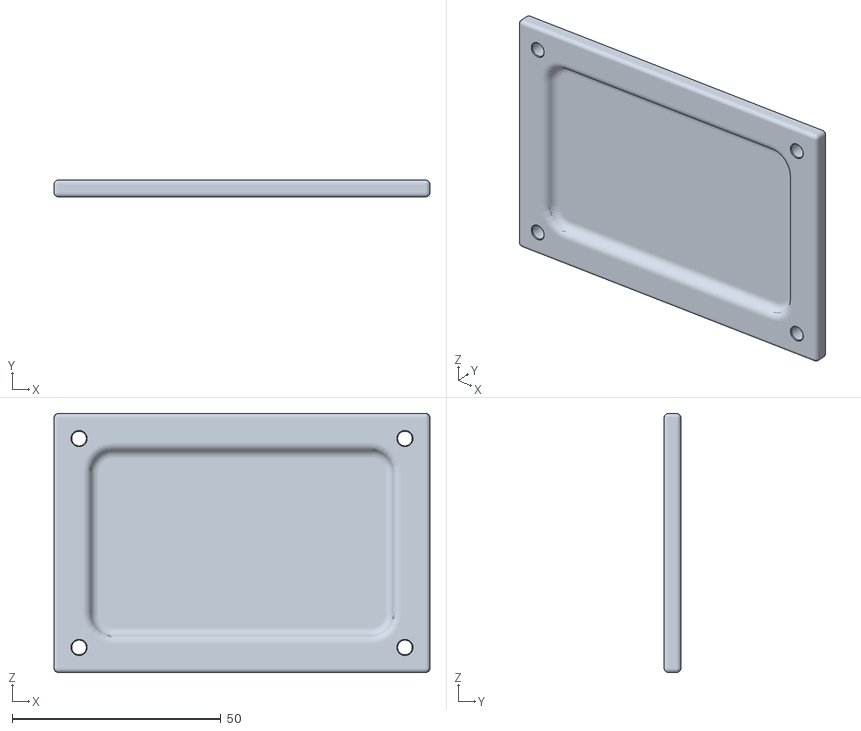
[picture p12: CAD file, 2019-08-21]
Documentation/Hardware/Enclosure - 3D Printing Model/STL Files/Solar_Panel_Lid.stl
90.0 x 4.00 x 62.0

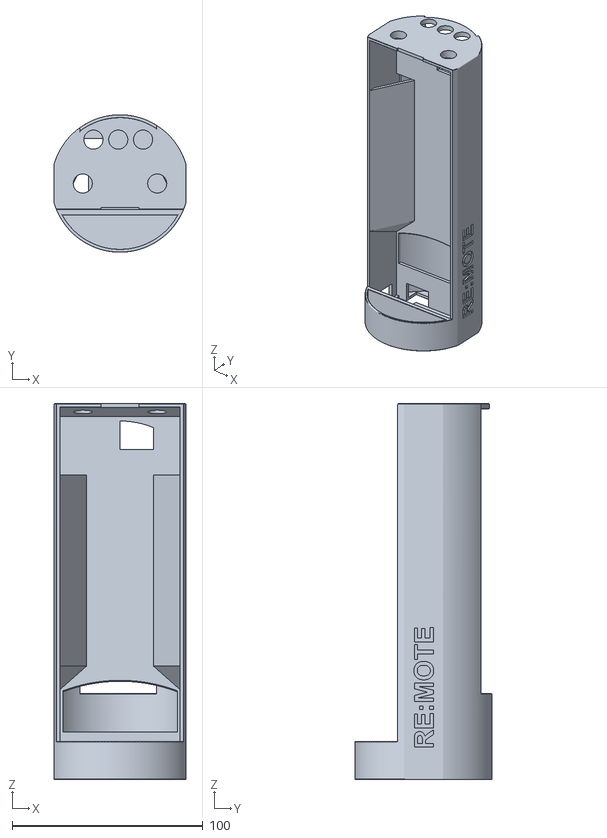
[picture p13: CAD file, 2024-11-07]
Documentation/Water_Sensor/3D_Printed_Enclosure/WS_Enclosure/v4/STL/re:mote-test4.stl
69.0 x 72.0 x 197.0

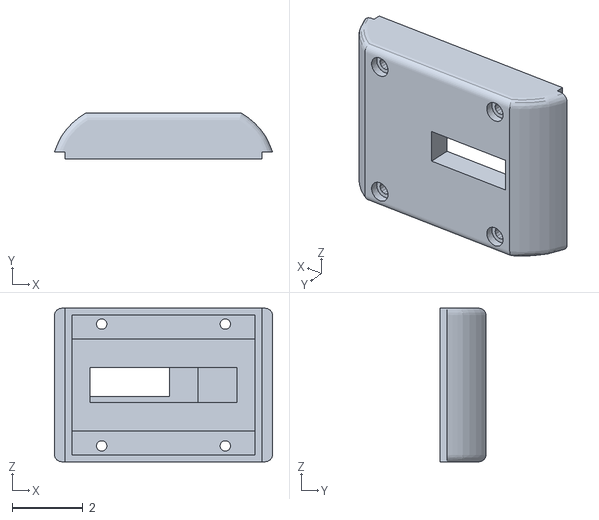
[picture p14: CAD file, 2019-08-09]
Research/Ryan_Notes/Turtle Tracker/Enclosure/Enclosure Designs/Tracker V4/Enclosure-Top.stl
6.17 x 1.30 x 4.35

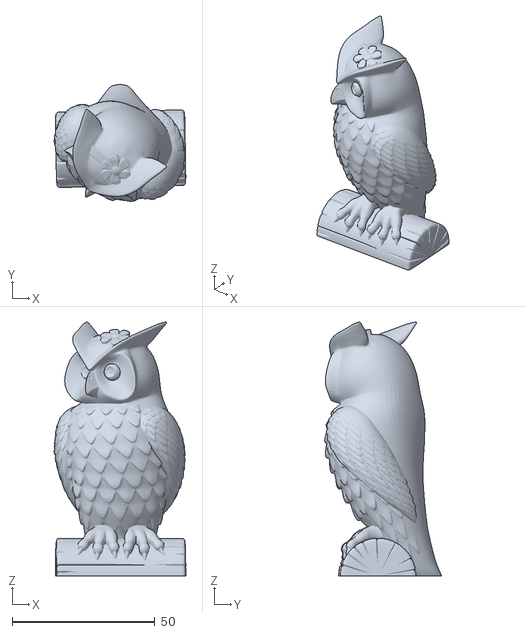
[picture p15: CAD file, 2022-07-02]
Turtle_Tracker/Docs/3D_Printed_Enclosure/Kobra_Manual/STL Files/owl.stl
46.1 x 40.9 x 89.1

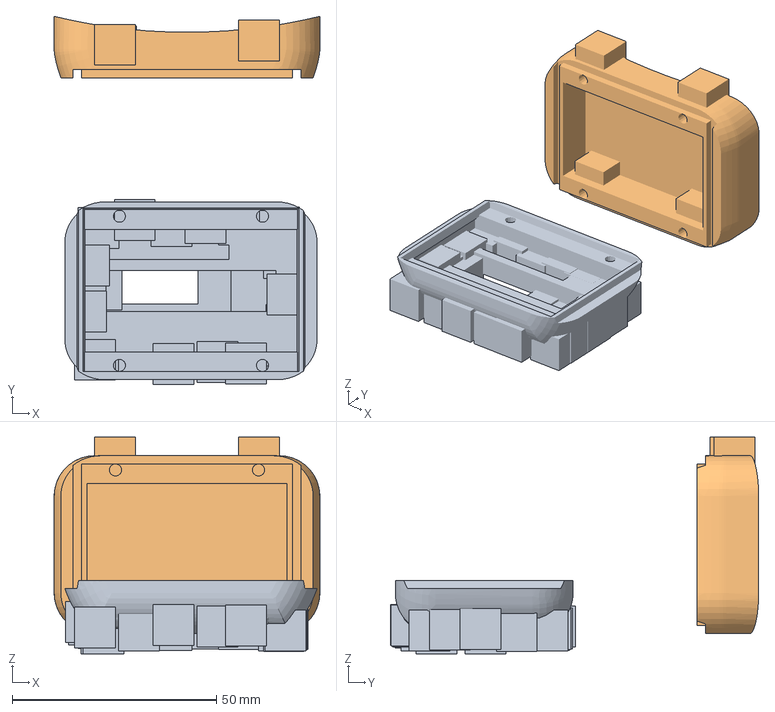
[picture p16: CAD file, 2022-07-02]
Turtle_Tracker/Docs/3D_Printed_Enclosure/Turtle_Tracker_Enclosure/v12/Cura/v12.3mf
65.0 x 90.0 x 53.0 mm

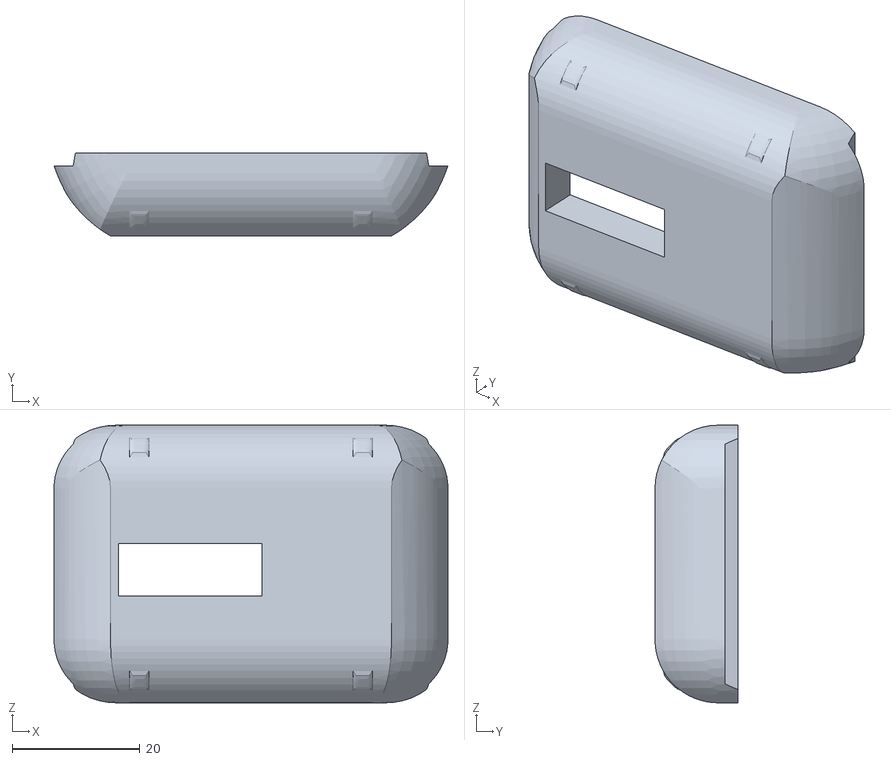
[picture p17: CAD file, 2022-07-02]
Turtle_Tracker/Docs/3D_Printed_Enclosure/Turtle_Tracker_Enclosure/v12/STL/Tracker_Enclosure-Top_2.stl
61.7 x 13.0 x 43.5

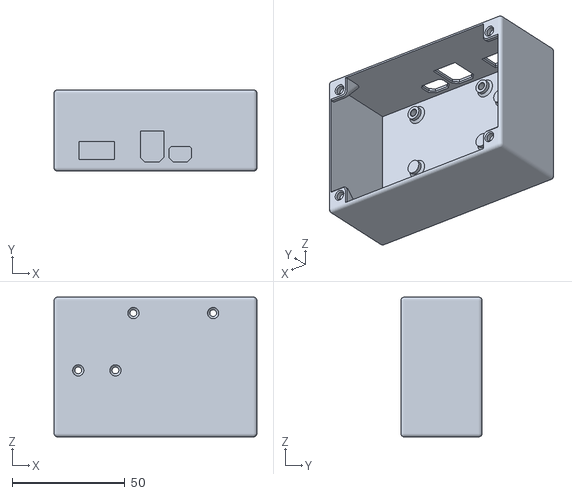
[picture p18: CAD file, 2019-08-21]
Documentation/Hardware/Enclosure - 3D Printing Model/STL Files/Solar_Panel_Box.stl
90.0 x 36.0 x 62.0

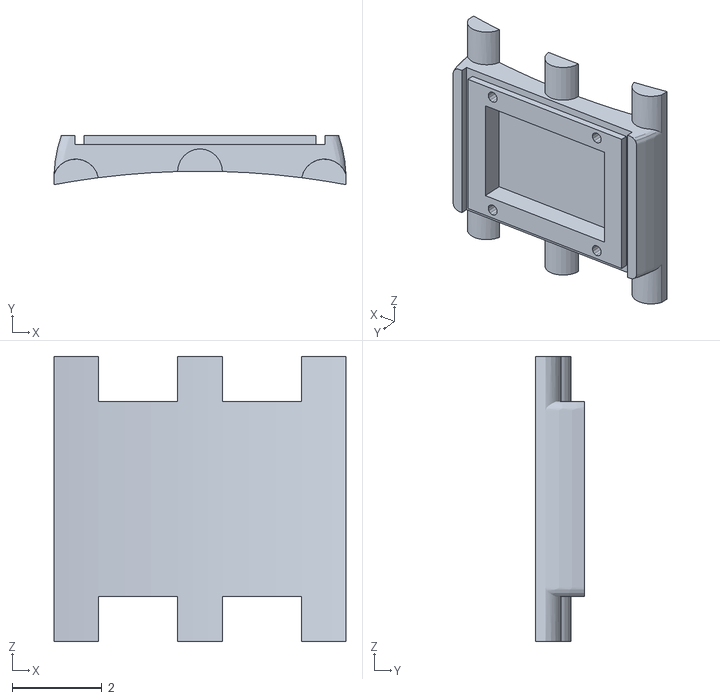
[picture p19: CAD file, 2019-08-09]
Research/Ryan_Notes/Turtle Tracker/Enclosure/Enclosure Designs/Tracker V4/Enclosure-Base.stl
6.50 x 1.10 x 6.35

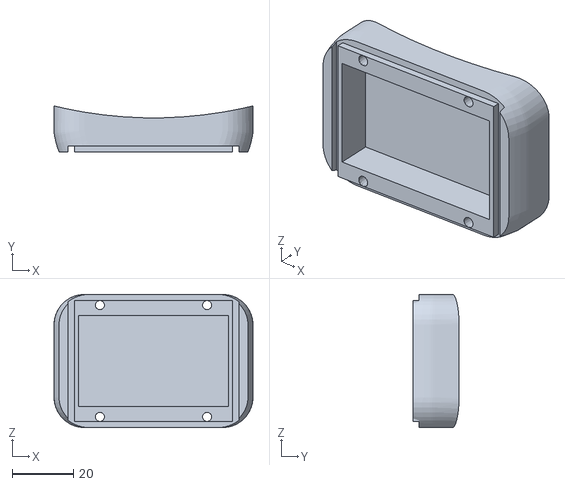
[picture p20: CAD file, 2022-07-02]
Turtle_Tracker/Docs/3D_Printed_Enclosure/Turtle_Tracker_Enclosure/v12/STL/Tracker_Enclosure-Base_1.stl
65.0 x 15.0 x 43.5

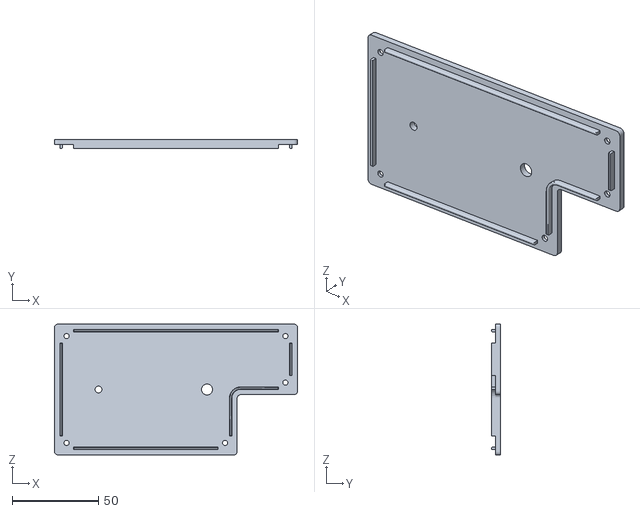
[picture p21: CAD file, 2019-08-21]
Documentation/Hardware/Enclosure - 3D Printing Model/STL Files/GATEWAYE_LID_Enclosure_Box.stl
141.0 x 5.50 x 76.0

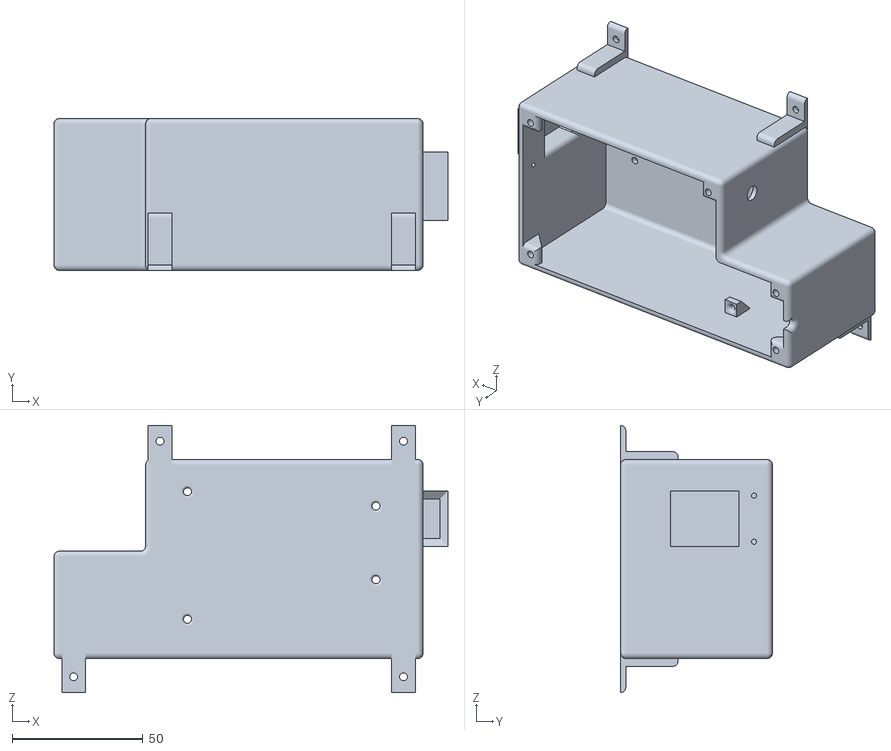
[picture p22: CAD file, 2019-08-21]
Documentation/Hardware/Enclosure - 3D Printing Model/STL Files/GATEWAY_Enclosure_Box.stl
150.5 x 58.0 x 102.0

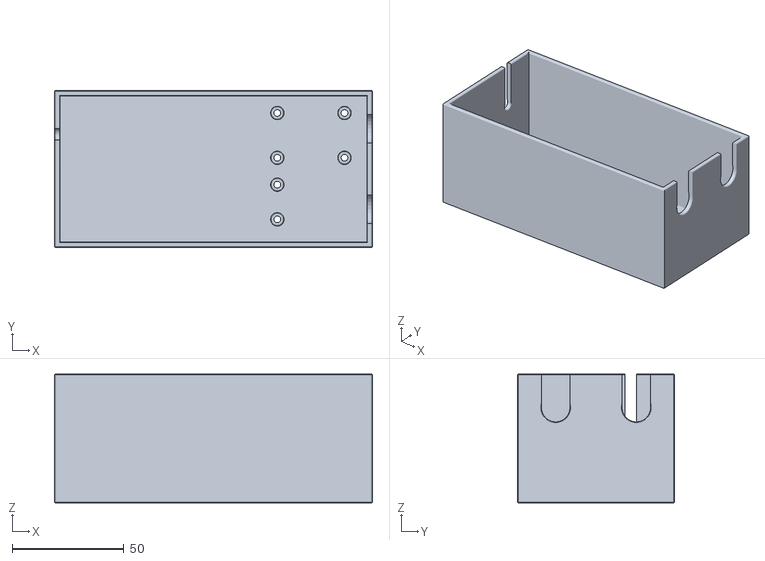
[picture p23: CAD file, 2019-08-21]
Documentation/Hardware/Enclosure - 3D Printing Model/STL Files/END_NODE_SIMPLE.stl
142.0 x 70.0 x 57.5

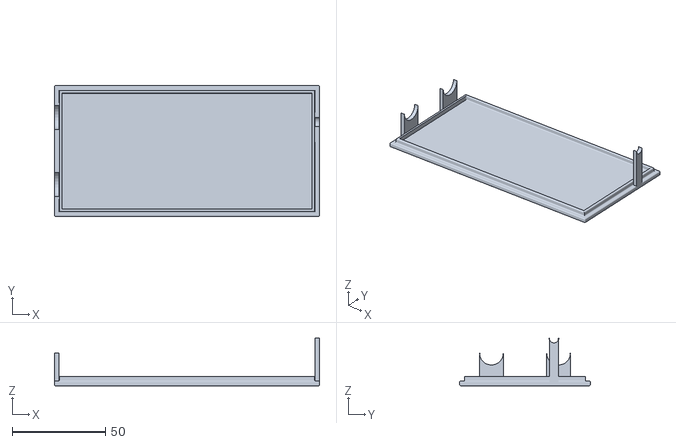
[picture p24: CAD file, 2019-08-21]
Documentation/Hardware/Enclosure - 3D Printing Model/STL Files/END_NODE_-_LID_SIMPLE.stl
142.0 x 70.0 x 25.5

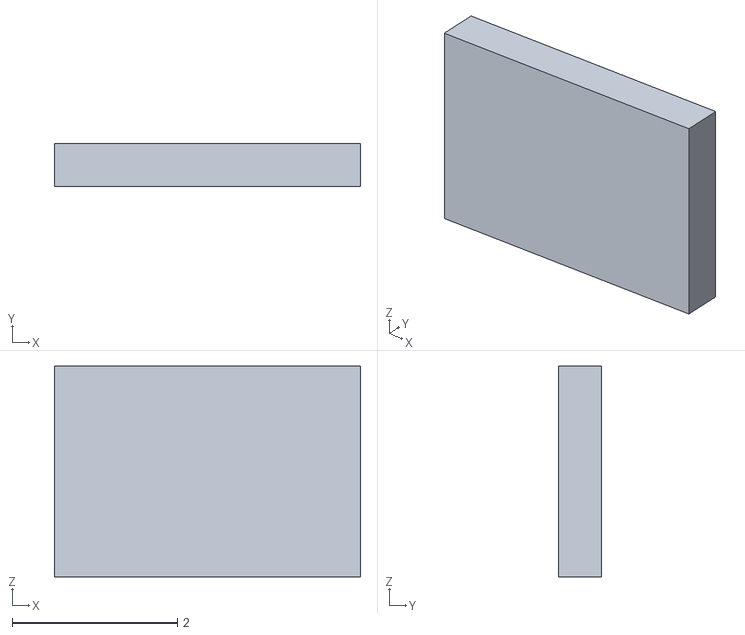
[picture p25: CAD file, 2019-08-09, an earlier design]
Research/Ryan_Notes/Turtle Tracker/Enclosure/Enclosure Designs/Tracker V2/3D Print Files/BatteryV2.stl
3.70 x 0.52 x 2.55

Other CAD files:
Turtle_Tracker/Docs/3D_Printed_Enclosure/Turtle_Tracker_Enclosure/v12/Inventer/Tracker.dwg
Research/Ryan_Notes/Turtle Tracker/Enclosure/Enclosure Designs/Tracker V2/3D Print Files/Case - BottomV2.stl
Documentation/Archive/Hardware/Enclosure - 3D Printing Model/End Node/END_NODE_-_LID_SIMPLE.ipt
Documentation/Archive/Hardware/Enclosure - 3D Printing Model/End Node/END_NODE_SIMPLE.ipt
Documentation/Archive/Hardware/Enclosure - 3D Printing Model/Gateway Node/Enclosure_Box.ipt
Documentation/Archive/Hardware/Enclosure - 3D Printing Model/Gateway Node/LID_Enclosure_Box.ipt
Documentation/Archive/Hardware/Enclosure - 3D Printing Model/Solar Power Enclosure/Solar_Module_Box.ipt
Documentation/Archive/Hardware/Enclosure - 3D Printing Model/Solar Power Enclosure/Solar_Module_Lid.ipt
Documentation/Hardware/Enclosure - 3D Printing Model/End Node/END_NODE_-_LID_SIMPLE.ipt
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

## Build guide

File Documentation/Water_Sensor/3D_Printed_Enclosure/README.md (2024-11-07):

# 3D Printing - Water Sensor Components Enclosure

## Overview

This document explains how to 3D print Water Sensor Components Enclosure by Anycubic Kobra (Other 3D printers may needs to use different profiles).

If you do not want to modify the enclosure model, skip to part 5.

## Preparation

- Anycubic Kobra or any 3D printer
- PETG Filament

## 1. Download Shapr3D

[Shapr3D](https://www.shapr3d.com)

Shapr3D's [educational license](hhttps://www.shapr3d.com/education) is free for students, teachers and faculty members of accredited educational institutions. The license is valid for one year (365 days) and can be renewed once it expires. 

## 2. Open project in Shapr3D

Open `.shapr` project file

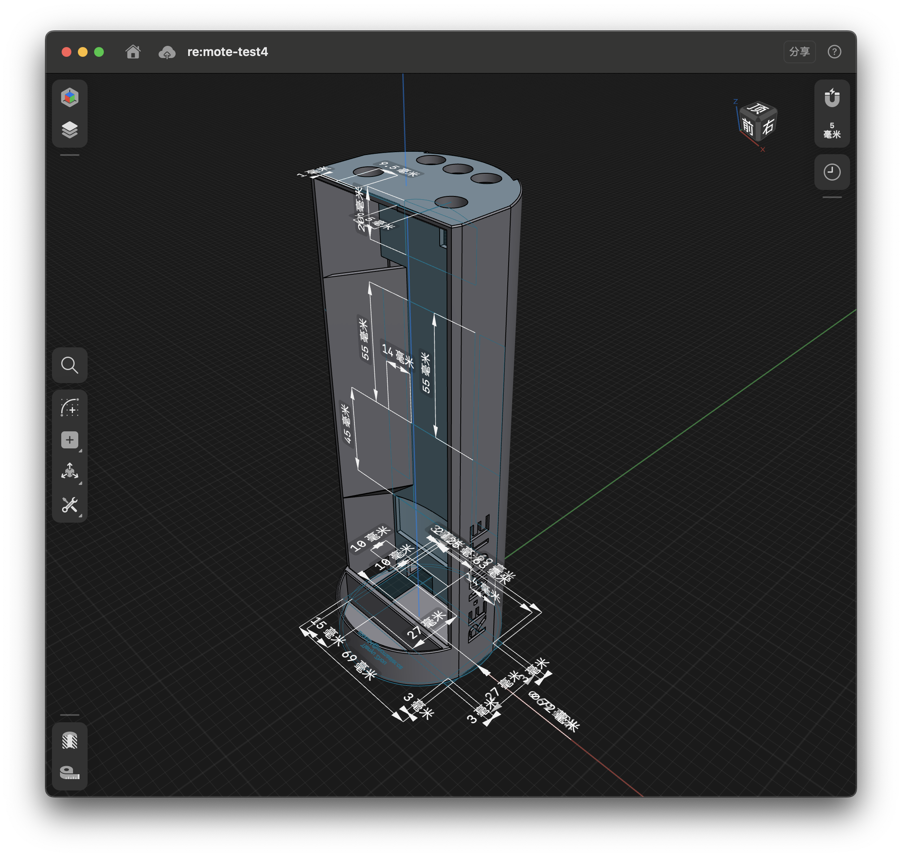
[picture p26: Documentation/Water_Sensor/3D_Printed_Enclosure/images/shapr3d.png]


Select `File` - `Export` - Choose `.stl` format- Click`Export`

## 3. Download and config Cura slicing software

#### Download

[Cura](https://github.com/Ultimaker/Cura/releases)

#### Config

Open Cura installation Folder

Windows version default location: `C:\Program Files\Ultimaker Cura <version>`

- Version 4.x
  Copy the folder `~/Printer Profile/resources` into the installation folder `Ultimaker Cura <version>/resources`

- Version 5.x
  Copy the folder `~/Printer_Profile/resources` into the installation folder `Ultimaker Cura <version>/share/cura/resources`

Open Cura and choose `Anycubic Kobra` printer with `Generic PETG` Filament

Click `Preferences` on the top bar, select `Configure Cura...`

Click on `Profiles`, then import `Printing_Profile/krunk.curaprofile`

## 4. Slice the model

Click `open` on the top left corner and select the stl file we generated in Inventor.



Align the models, and make sure there is some space between them.

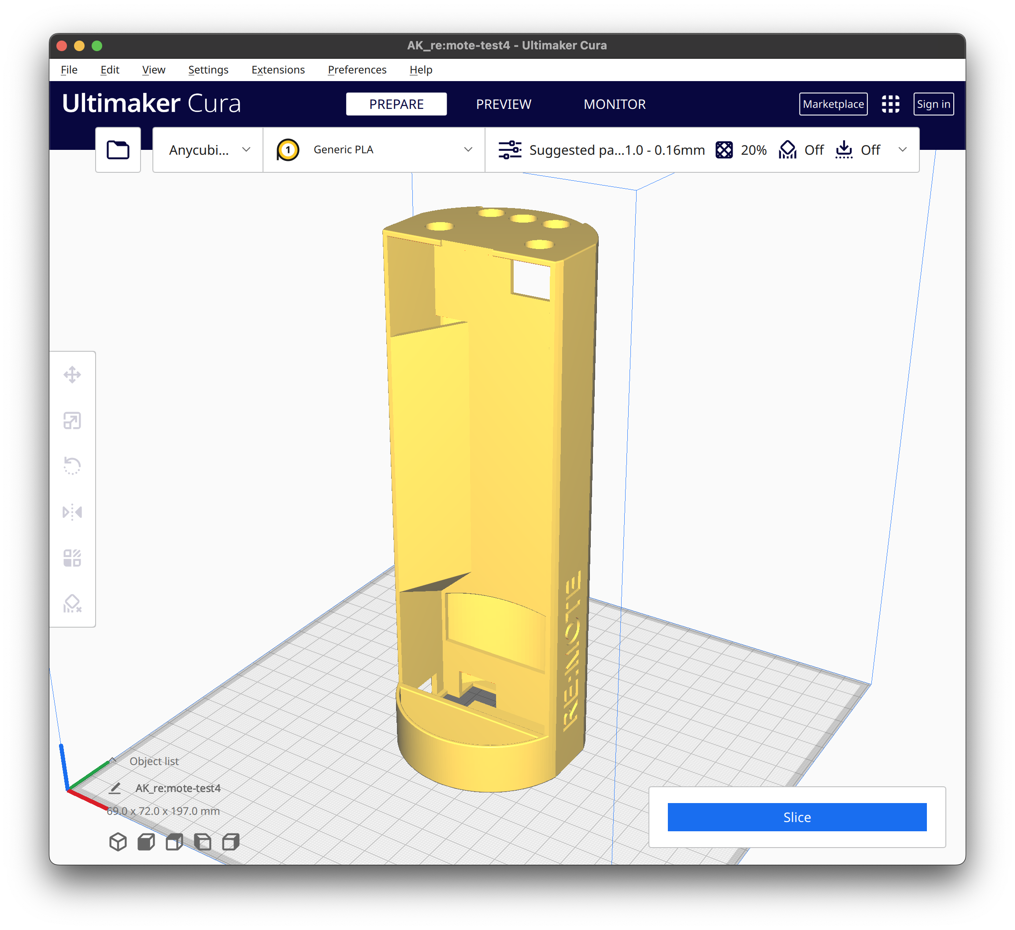
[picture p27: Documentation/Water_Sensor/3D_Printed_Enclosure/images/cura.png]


Select the profile we just imported

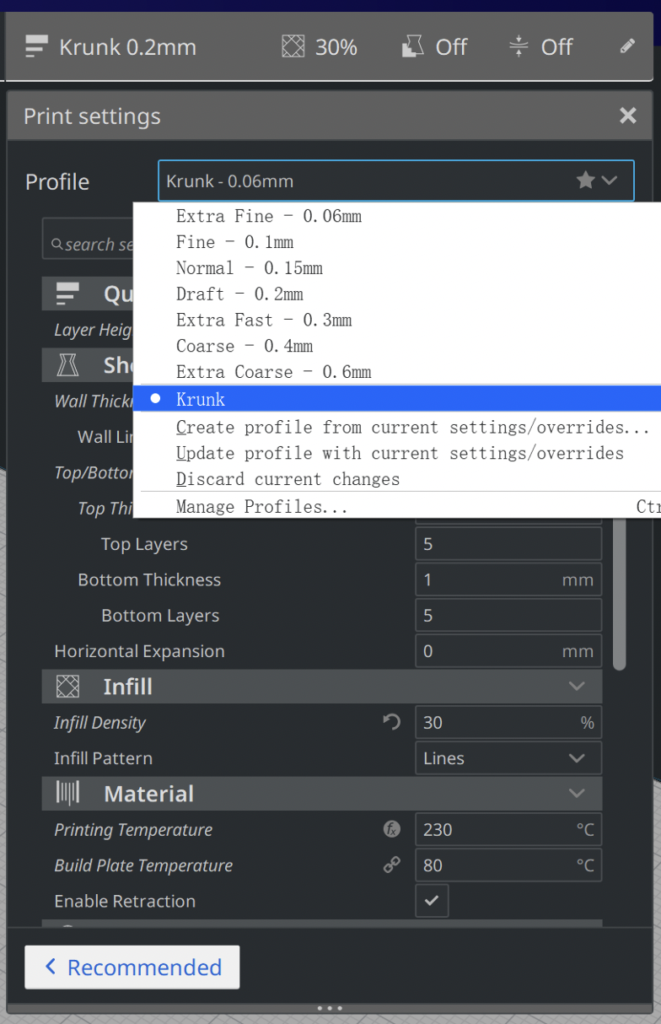
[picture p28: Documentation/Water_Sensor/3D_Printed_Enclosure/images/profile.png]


Click `slice` then `Save to file`

## 5. Copy gcode to SD card

Once sliced the model, a gcode file will be generated.

If you are not updating the model, use the `.gcode` file under `./WS_Enclosure` folder

Copy the file into a MicroSD card

## 6. Start printing

[Kobra Manual](Turtle_Tracker/Docs/3D_Printed_Enclosure/Kobra_Manual/User%20Manual/Anycubic%20Kobra_User%20Manual_20211227_V0.0.1.pdf)

- Leveling: page 25 - 27
- Loading Filament: page 28 - 31
- Printing Models: page 32

<p float="left">
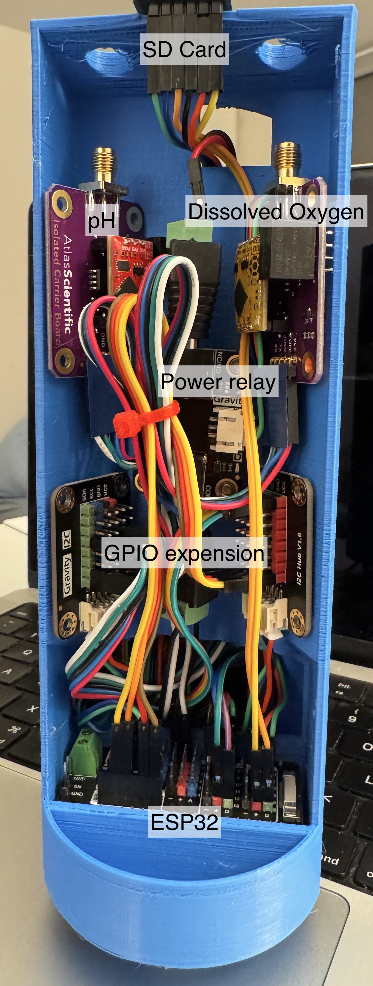
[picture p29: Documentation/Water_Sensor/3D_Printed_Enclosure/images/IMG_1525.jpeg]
  
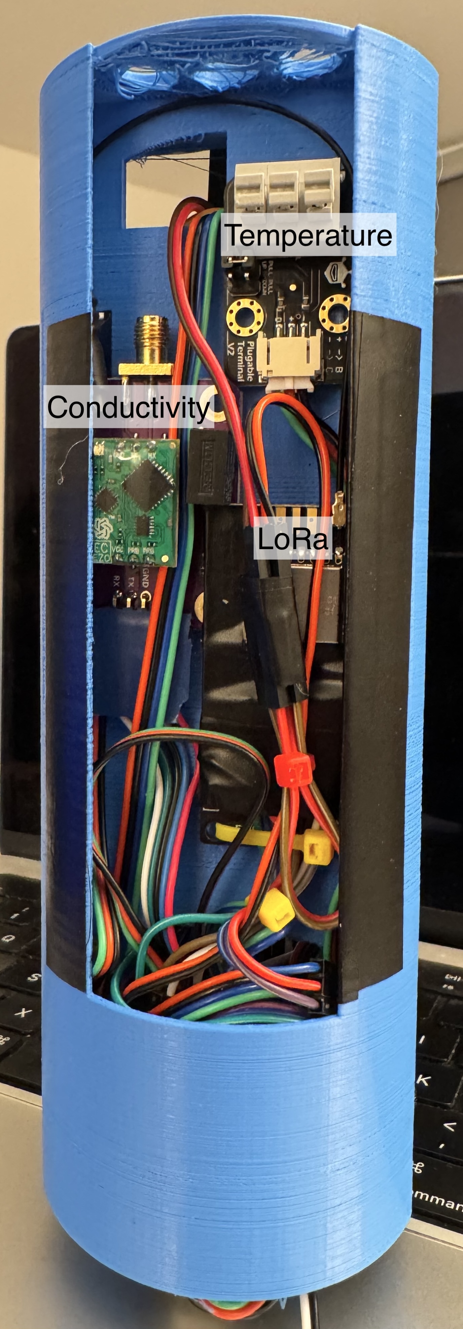
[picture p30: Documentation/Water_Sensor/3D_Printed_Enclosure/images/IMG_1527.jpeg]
  
</p>

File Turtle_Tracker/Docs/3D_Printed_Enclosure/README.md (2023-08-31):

# 3D Printing - Turtle Tracker Enclosure

## Overview

This document explains how to 3D print Turtle Tracker Enclosure by Anycubic Kobra (Other 3D printers may needs to use different profiles).

If you do not want to modify the enclosure model, skip to part 5.

## Preparation

- Anycubic Kobra
- PETG Filament
- #5x5/8 Screws with Flat Socket Head

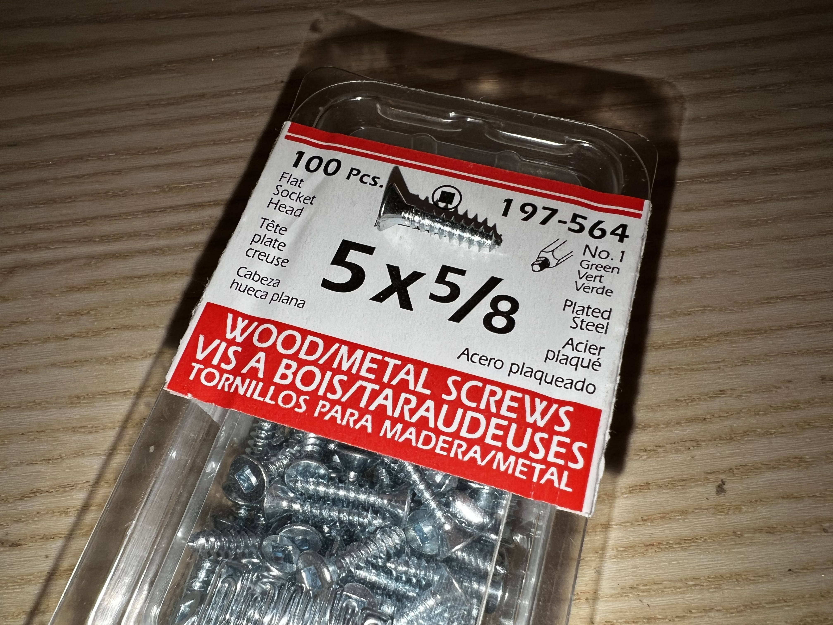
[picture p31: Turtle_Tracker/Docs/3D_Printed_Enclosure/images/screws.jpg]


## 1. Download Autodesk Inventor

[Autodesk Inventor](https://www.autodesk.com/products/inventor/overview)

Students and educators can get educational access to Autodesk Inventor. [Autodesk Educational Access](https://www.autodesk.com/education/edu-software/overview)

## 2. Open project in Inventor

Open `.iam` project file

Select `File` - `Output` - `CAD File` - Choose `.stl` format

## 3. Download and config Cura slicing software

#### Download

[Cura](https://github.com/Ultimaker/Cura/releases)

#### Config

Open Cura installation Folder

Windows version default location: `C:\Program Files\Ultimaker Cura <version>`

- Version 4.x
  Copy the folder `~/Printer Profile/resources` into the installation folder `Ultimaker Cura <version>/resources`

- Version 5.x
  Copy the folder `~/Printer_Profile/resources` into the installation folder `Ultimaker Cura <version>/share/cura/resources`

Open Cura and choose `Anycubic Kobra` printer with `Generic PETG` Filament

Click `Preferences` on the top bar, select `Configure Cura...`

Click on `Profiles`, then import `Printing_Profile/krunk.curaprofile`

## 4. Slice the model

Click `open` on the top left corner and select the stl file we generated in Inventor.



Align the models, and make sure there is some space between them.



Select the profile we just imported



Click `slice` then `Save to file`

## 5. Copy gcode to SD card

Once sliced the model, a gcode file will be generated.

If you are not updating the model, use the `.gcode` file under `./Turtle_Tracker_Enclosure` folder

Copy the file into a MicroSD card

## 6. Start printing

[Kobra Manual](Turtle_Tracker/Docs/3D_Printed_Enclosure/Kobra_Manual/User%20Manual/Anycubic%20Kobra_User%20Manual_20211227_V0.0.1.pdf)

- Leveling: page 25 - 27
- Loading Filament: page 28 - 31
- Printing Models: page 32

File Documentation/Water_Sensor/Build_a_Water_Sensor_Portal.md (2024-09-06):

# Build a Water Sensor

### Depending on your network preference, select one of the options provided below.

<details>
<summary>Using LoRa with one or more gateways</summary>
<br>

This approach employs a mesh network, ideal for situations where the 3G signal is unstable or unavailable over water.

<div align="center">
    
</div>

A gateway is essential to facilitate the transmission of data from the node to the server.

## Build a Sensor Node

Link: [Build EndNode](/Documentation/Water_Sensor/Build_EndNode.md)

### Connect LoRa Module

**LoRA:**

- Total of 7 pins on the chip: Used Tx, Rx, Vcc and GND <u>(IGNORE SET, AUX and EN pins)</u>.
- Connect the Vcc of LoRA to the 5V of Arduino. Second, the GND of LoRA with GND.
- Connect LoRA Tx with Arduino A4.
- Connect LoRA Rx with Arduino A5.

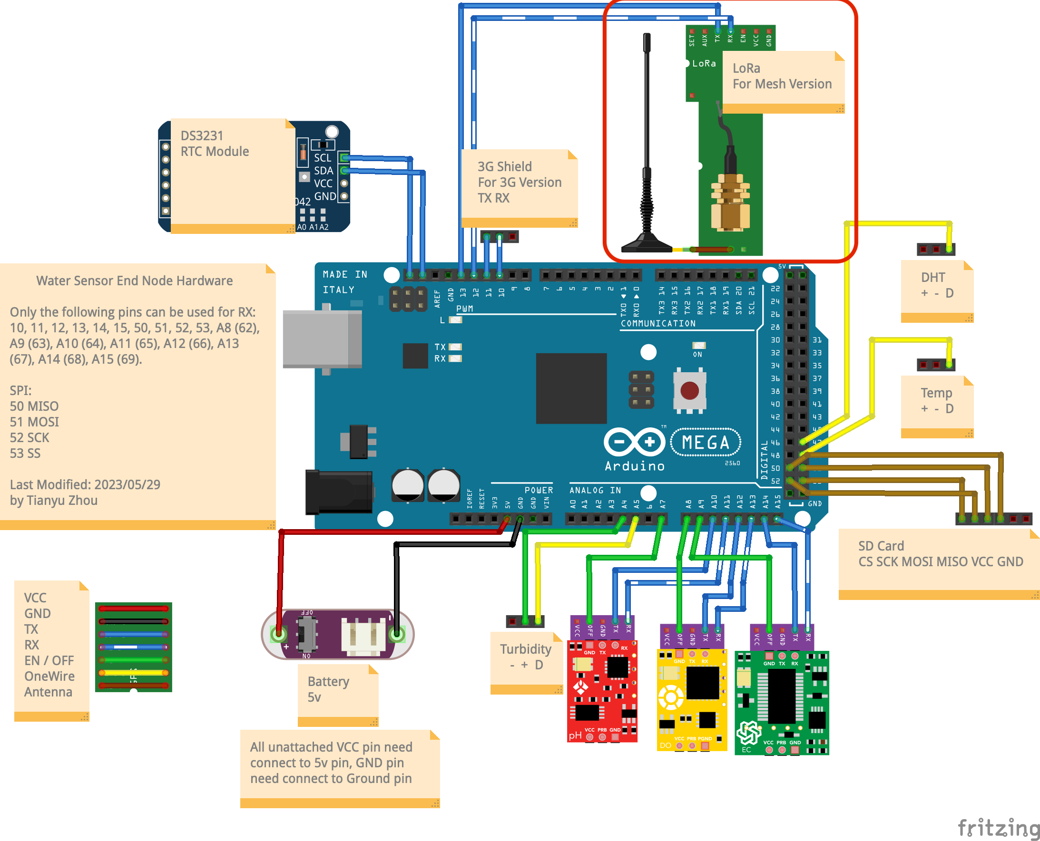
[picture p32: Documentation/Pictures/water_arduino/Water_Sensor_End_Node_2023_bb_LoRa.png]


## Build gateway

Link: [Build Gateway](/Documentation/Water_Sensor/Build_Gateway.md)

Link: [Gateway Enclosure](/Documentation/Water_Sensor/Gateway_Enclosure_Assembly.md)

## Upload firmware for nodes

### remoteConfig.h

The primary configuration file is remoteConfig.h, located within the `Arduino/libraries/re-moteConfig/` directory. To configure your Arduinos:

1. Navigate to the re-moteConfig library: `Arduino/libraries/re-moteConfig/remoteConfig.h`.
2. This is the sole file you'll need to modify unless you're introducing custom functionalities.
3. Within the file, comment or uncomment lines as per your desired configuration.
4. Adjust the `Node_Type` value based on whether you're working with a Gateway or an End node.
5. Each setting within the file comes with comprehensive comments to guide you on its purpose and function.
6. Ensure you follow the instructions carefully for optimal performance.

To configure the sensor node, refer to the example provided below.

[Mesh remoteConfig.h](Water_Sensor/Libraries/re-moteConfig/Example/meshNode.h)

### Upload

Link: [Upload firmware](/Documentation/Water_Sensor/Upload_firmware.md)

## Upload firmware for Gateway

### remoteConfig.h

The primary configuration file is remoteConfig.h, located within the `Arduino/libraries/re-moteConfig/` directory. To configure your Arduinos:

1. Navigate to the re-moteConfig library: `Arduino/libraries/re-moteConfig/remoteConfig.h`.
2. This is the sole file you'll need to modify unless you're introducing custom functionalities.
3. Within the file, comment or uncomment lines as per your desired configuration.
4. Adjust the `Node_Type` value based on whether you're working with a Gateway or an End node.
5. Each setting within the file comes with comprehensive comments to guide you on its purpose and function.
6. Ensure you follow the instructions carefully for optimal performance.

To configure the gateway node, refer to the example provided below.

[Mesh remoteConfig.h](Water_Sensor/Libraries/re-moteConfig/Example/meshNode.h)

### Upload

Link: [Upload firmware](/Documentation/Water_Sensor/Upload_firmware.md)

</details>

---

<details>
<summary>Using 3G on sensor node without gateway</summary>
<br>

This approach involves equipping all sensor nodes with celluar connectivity. It's ideal for setups where all nodes are within areas with available celluar signals and are spaced at considerable distances from one another.

<div align="center">
    
</div>

## Build a Sensor Node

Link: [Build EndNode](/Documentation/Water_Sensor/Build_EndNode.md)

## Connect the 3G Module

**3G shield:**

- Total of 7 pins on the chip: Used Tx, Rx, Vcc and GND <u>(IGNORE SET, AUX and EN pins)</u>.
- Attach celluar shield to Arduino Mega or only connect the pins.
- Connect 3G Tx with Arduino 11.
- Connect 3G Rx with Arduino 10.

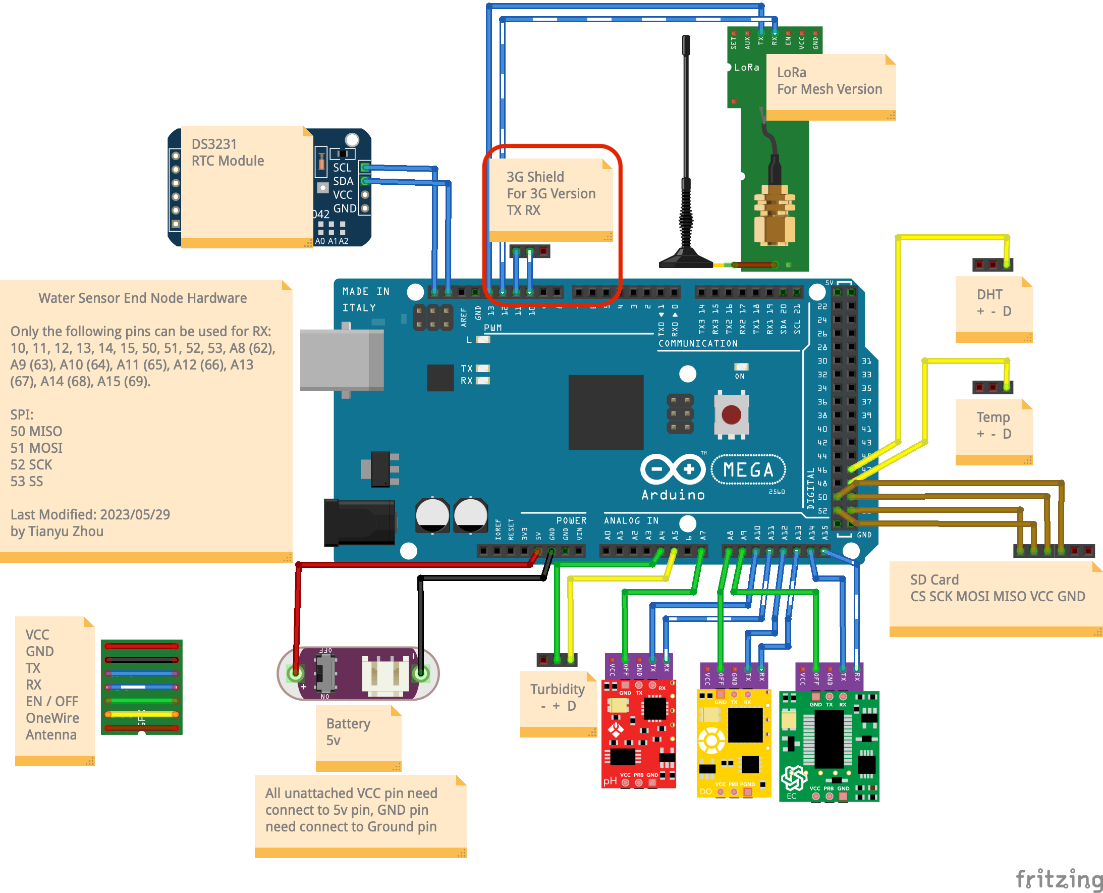
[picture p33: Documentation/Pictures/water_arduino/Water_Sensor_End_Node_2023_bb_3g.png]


## Upload firmware for nodes

### remoteConfig.h

The primary configuration file is remoteConfig.h, located within the `Arduino/libraries/re-moteConfig/` directory. To configure your Arduinos:

1. Navigate to the re-moteConfig library: `Arduino/libraries/re-moteConfig/remoteConfig.h`.
2. This is the sole file you'll need to modify unless you're introducing custom functionalities.
3. Within the file, comment or uncomment lines as per your desired configuration.
4. Each setting within the file comes with comprehensive comments to guide you on its purpose and function.
5. Ensure you follow the instructions carefully for optimal performance.

To configure the sensor node, refer to the example provided below.

[3G remoteConfig.h](Water_Sensor/Libraries/re-moteConfig/Example/singleNode.h)

### Upload

Link: [Upload firmware](/Documentation/Water_Sensor/Upload_firmware.md)

</details>

---

<details>
<summary>Using as a data logger and store data on the SD card without uploading to server</summary>
<br>

This option is suitable if you don't require real-time data and prefer to retrieve information solely from an SD card.

<div align="center">
    
</div>

## Build a Sensor Node

Link: [Build EndNode](/Documentation/Water_Sensor/Build_EndNode.md)

## Upload firmware for nodes

### remoteConfig.h

The primary configuration file is remoteConfig.h, located within the `Arduino/libraries/re-moteConfig/` directory. To configure your Arduinos:

1. Navigate to the re-moteConfig library: `Arduino/libraries/re-moteConfig/remoteConfig.h`.
2. This is the sole file you'll need to modify unless you're introducing custom functionalities.
3. Within the file, comment or uncomment lines as per your desired configuration.
4. Each setting within the file comes with comprehensive comments to guide you on its purpose and function.
5. Ensure you follow the instructions carefully for optimal performance.

To configure the sensor node, refer to the example provided below.

[dataLogger remoteConfig.h](Water_Sensor/Libraries/re-moteConfig/Example/dataLogger.h)

### Upload

Link: [Upload firmware](/Documentation/Water_Sensor/Upload_firmware.md)

</details>

<br><br><br>

## Build a Pipe Enclosure

Link: [Pipe Enclosure Assembly](/Documentation/Water_Sensor/Pipe_Enclosure_Assembly.md)

## Calibrate Sensors

Link: [Sensors Calibration](/Documentation/Water_Sensor/Sensors_Calibration.md)

# Testing

It's important to test your setup at every stage of this document to make sure everything is functioning correctly. It is also highly recommended that once everything is finished, you run a full test over the course of a few days. This will ensure that everything is functioning as expected.

# Deploying

Once everything is completely ready to be deployed, it is important to deploy them correctly. The first step is to choose your deployment location carefully. The LoRa mesh modules used allow for your nodes to be set up in a mesh configuration, which means that as long as a node (node 1) is within range of any other node (node2) that is connected to a gateway, the first node (node 1) will be able to connect to the gateway. This allows for a long string of end nodes connected to each other and only one gateway. The tested range of these LoRa mesh modules is about 200m through heavy obstruction (hill, buildings, etc.), about 500m through light obstruction (trees, etc.), and 650m through very light obstruction (chain link fences, nothing, etc.). This range can be improved by lifting the antenna, but by how much depends heavily on your circumstances (tested up to about +100m). It is also important to consider the legality of your deployment locations; you must ensure that you are not breaking any laws by deploying your nodes in the locations.

The next thing to consider when deploying your nodes is hardware safety. It is important to make sure that your nodes will not be dislodged or washed away by heavy rains, strong winds, or snow (depending on the weather where you're deploying). Depending on your deployment locations, it may also be important to consider hiding/securing your nodes in some way to prevent vandalism. This could be done by burying your nodes (although this may affect GPS and LoRa connectivity), painting them to blend in, or covering them with something (could be leaves, or even trash, etc.).

Once the nodes have been secured, it is important to deploy the sensors so that they are secure. For us, this involved putting an anchor into the water and securing the sensor probes to it using waterproof tape. The steps to do this will depend on the location and sensor probes you are using.

# Troubleshooting

The first step to troubleshooting is to make sure you've configured and connected everything correctly. If that doesn't help, the next step is to identify the problem. This is most easily done by isolating parts of the Arduino and seeing which ones function correctly and which ones do not. If you've been testing after every step of this document, this should be quite easy. Once you've isolated the problem (let's say your DO sensor isn't initializing), it is good practice to re-check the configuration for this module to make sure that isn't the cause of the problem. If that wasn't the problem, you then need to determine if the problem is with the module or the Arduino. This is most easily done if you have another Arduino or sensor to swap in. If not, you can try to change the pins the sensor is connected to (ideally to pins you know work). If the problem is with the sensor, you may have gotten a defective one and will have to contact the seller. If the issue is with the Arduino, you can try changing the pins the sensor is connected to to see if some of the pins are broken. If that doesn't help, try testing the Arduino with a simple LED blink sketch. If the module and Arduino work separately, but not together, you will have to do proper software bug finding and fixing, for which it is recommended that you have some form of experience with software development, preferably in Arduino or C/C++.

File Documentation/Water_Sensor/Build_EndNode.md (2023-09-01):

# Build a Sensor Node

## Get all parts ready.

[Specification](/Documentation/Water_Sensor/Specification.md)

## Arduino Assembly

**KEY POINTS:**  

- All modules have a power pin (commonly known as Vcc) and a ground pin (GND).

- Vcc pin of all the modules must be connected to the 5V pin of Arduino. 

  - Before connecting any sensors to the 5V supply from the Arduino, make sure that the sensors can operate at the 5V input supply. This can be easily confirmed from the product datasheet.

- For all of the modules except the Turbidity sensor, pins such as Rx (Receiving), Tx (Transmitting), and En (Enable) or OFF can be connected to either analog or digital input/output pins of Arduino. This is because Arduino's analog pins can be easily configured and used as digital I/O pins.
  - In this project, the Turbidity sensor is transceiving signals in analog form. Please remember to only connect the turbidity sensors data pin to an analog pin of Arduino.

- After you have finished connecting all the pins as discussed below, keep in mind that you are required to switch the Rx and Tx pins of all the sensors (except temperature and turbidity sensors) in the software.

- In the software, Arduino's digital I/O pins can be assigned by using their pin numbers, and Arduino Nano has 13 digital I/O pins. In case analog pins are needed to function as digital I/O pins, use the following numbers:

  | Analog pins | Designated Number for the Software |
  | ----------- | ---------------------------------- |
  | A0          | 14                                 |
  | A1          | 15                                 |
  | A2          | 16                                 |
  | A3          | 17                                 |
  | A4          | 18                                 |
  | A5          | 19                                 |

Using [IO Sensor Shield For Arduino Mega](https://www.dfrobot.com/product-560.html) can make cable connection easier.

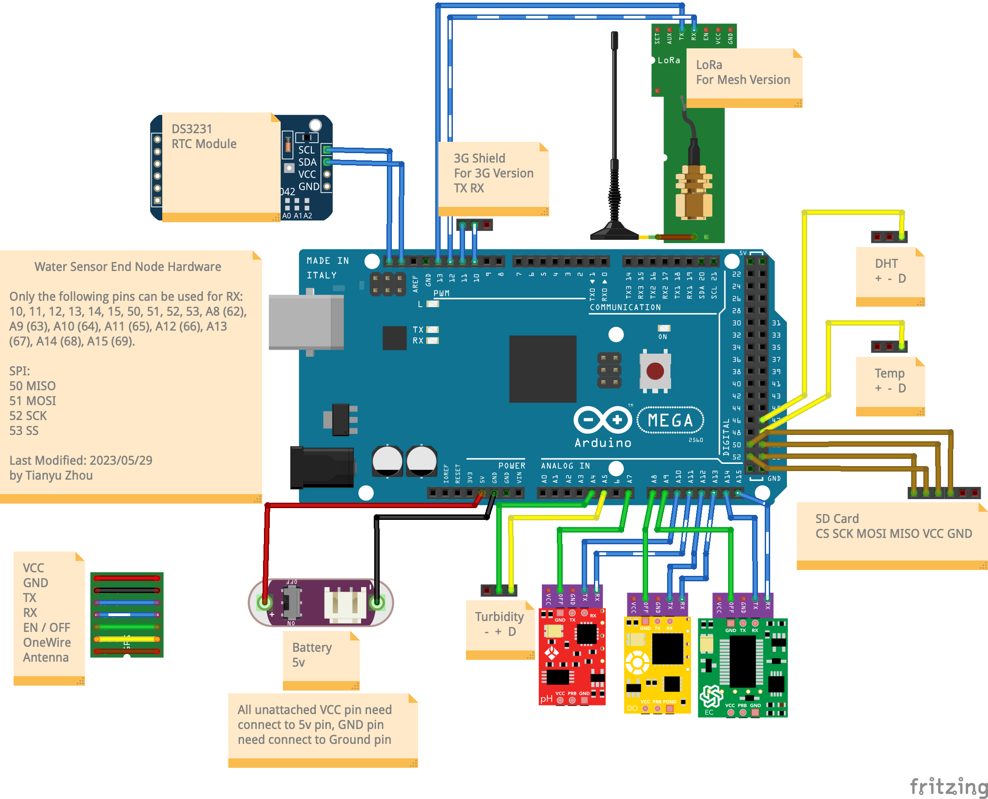
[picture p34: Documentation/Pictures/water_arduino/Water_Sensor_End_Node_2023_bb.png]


**pH Sensor:**

- Connect PH-Vcc to Arduino-5V
- Connect PH-GND to Arduino-GND
- Connect PH-OFF to Arduino-A7
- Connect PH-Tx to Arduino-A10
- Connect PH-Rx to Arduino-A11

**Electrical Conductivity (EC) Sensor:**

- Connect EC-Vcc to Arduino-5V
- Connect EC-GND to Arduino-GND
- Connect EC-OFF to Arduino-A9
- Connect EC-Rx to Arduino-A15
- Connect EC-Tx to Arduino-A14

**Dissolved Oxygen (DO) Sensor:**

- Connect DO-Vcc to Arduino-5V
- Connect DO-GND to Arduino-GND
- Connect DO-OFF to Arduino-A8
- Connect DO-Tx to Arduino-D12
- Connect DO-Rx to Arduino-D13

**Turbidity Sensor:**

- Connect Turbidity-PWR to Arduino-A4
- Connect Turbidity-GND to Arduino-GND
- Connect Turbidity-D to Arduino-A5
Important Note: Turbidity's Data pin needs analog connection to the Arduino

**Temperature Sensor:**

- Connect Temperature-Vcc to Arduino-5V
- Connect Temperature-GND to Arduino-GND
- Connect Temperature-D to Arduino-D49

## Completed Arduino

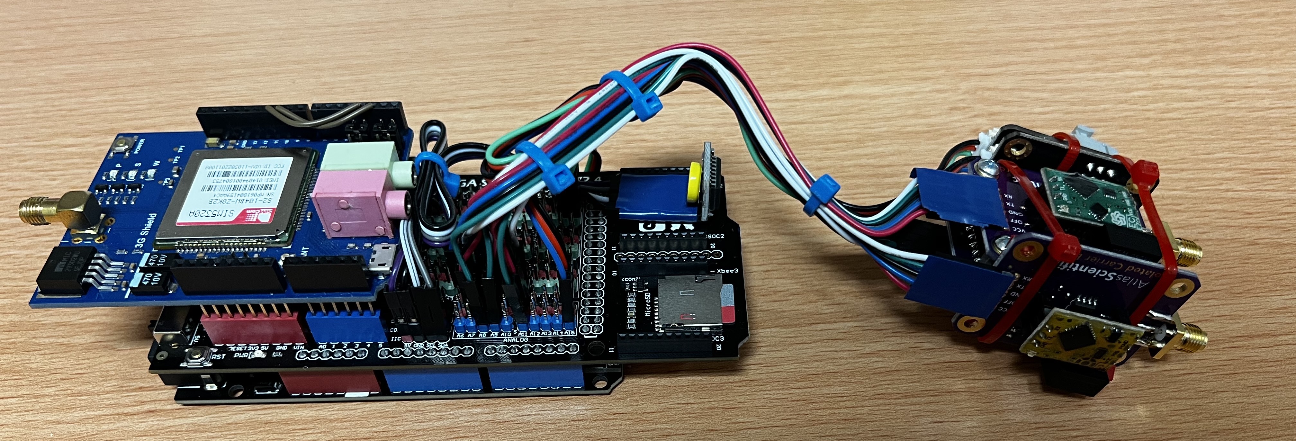
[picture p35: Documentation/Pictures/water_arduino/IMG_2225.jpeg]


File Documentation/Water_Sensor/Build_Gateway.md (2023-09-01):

# Build a Gateway

## Get all parts ready.

[Specification](/Documentation/Water_Sensor/Specification.md)

## Breakdown of all connections:

**SD Card:**

This module requires SPI communication with the Arduino. Thus, it is imperative to read about the SPI pins of the specific Arduino board you will be using. This information can be found in the 'Input and Output' section of your Arduino Board. Arduino Uno in the specification page is supported as following pins.

- Connect SD-Card-CS to Arduino D10
- Connect SD-Card-SCK to Arduino D13
- Connect SD-Card-MOSI to Arduino D11
- Connect SD-Card-MISO to Arduino D12
- Connect SD-Card-Vcc to Arduino 5V
- Connect SD-Card-GND to Arduino GND

**DHT22 Sensor:**

- Connect DHT-Vcc to Arduino 5V
- Connect DHT-GND to Arduino GND
- Connect DHT-D to Arduino D5

**FONA 3G by Adafruit:**

- Connect FONA-Vcc to Arduino 5V
- Connect FONA-GND to Arduino GND
- Connect FONA-Rx to Arduino D4
- Connect FONA-Tx to Arduino D3
- Connect FONA-Key to Arduino D2

**LoRA:**

- Total of 7 pins on the chip: Used Tx, Rx, Vcc, and GND (IGNORE SET, AUX, and EN pins)
- Connect the Vcc of LoRA to the 5V of Arduino Nano
- Connect GND of LoRA to GND of Arduino Nano
- Connect LoRA Tx to Arduino D6
- Connect LoRA Rx to Arduino D7

------

#### Optimize battery life (Optional and require soldering skill):

- Remove unnecessary LEDs and voltage regulator from the Arduino or any other module. 

  <u>Need to know how?</u> Click on [Link#1](http://www.home-automation-community.com/arduino-low-power-how-to-run-atmega328p-for-a-year-on-coin-cell-battery/), [Link#2](https://www.youtube.com/watch?v=2nNz0faMti0), [Link#3](https://www.youtube.com/watch?v=2xVOg7nYH-E), [Link#4](https://www.youtube.com/watch?v=7qujkC72dYs)

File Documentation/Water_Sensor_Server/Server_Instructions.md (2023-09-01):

# **How to access RaspberryPi (RPi) on windows OS?** 

If you already know the IP address/hostname of your RPi, you can login by following the steps below (otherwise start from the RPi setup - given after step 3's completion):
The following steps are for SSH connection:

1. Download and install PuTTY software using: <https://www.putty.org/>

2. Open PuTTY software: 

In the ‘*Host Name (or IP address)*’ section, 

use the IP address of the website (e.g. ###.###.##.###) – without port number 

*or* 

use the hostname and hit ‘Enter’.

If prompted, say ‘Yes’ to the ‘PuTTY Security Alert’

3. This will open a command prompt, asking you to login:

Login as: <u>user</u>

user@ip_address’s password: <u>password</u>

NOTE: Both <u>user</u> and <u>password</u> details are to be filled in by the user

Congrats! You have successfully logged into the RaspberryPi. Now, you can communicate through an SSH connection to your RaspberryPi from the windows desktop.

# How to setup RaspberryPi as a webserver using Windows Computer?

First, let's install an operating system on RPi:
<br />
To begin, you will need the following to complete this process:

\-          RaspberryPi 

\-          MicroSD Card (and an adapter to plug it into your computer)

\-          Micro-USB Power Cable

\-          RJ45 Ethernet Cable (Standard Ethernet Cable)

Software Requirement:

\-          Download ‘Raspbian Stretch with desktop and recommended software’ using: <https://www.raspberrypi.org/downloads/raspbian/> (Use either Torrent or ZIP option)

\-          Download and install the recommended extraction software ‘7-zip’ to extract the image file from the ZIP version of Raspbian, using: <https://www.7-zip.org/download.html> 

(NOTE: This software may not be needed as windows has a standard extraction tool)

\-          Download and install SSH client using: <https://www.chiark.greenend.org.uk/~sgtatham/putty/latest.html>

\-          Download and install Win32 Disc Imager using: 					<https://sourceforge.net/projects/win32diskimager/files/latest/download>

<br /><br /><br /> 

<u>Option #1</u>: SSH connection with RaspberryPi (Headless Method - without the need of a keyboard and a mouse attached to the RaspberryPi)

**STEP 1**: Right-click on the Raspbian Operating System file (zip file), and using the 7-zip tool extract the file in a folder

**STEP 2**: Insert a Micro-SD card into your computer

**STEP 3**: Open Win32DiskImager:

a.       Under the Image File section, hit the folder button to navigate and select the extracted image file (extracted file in step 1)

b.       Under the Device column, select Micro-SD card drive

c.       Hit ‘Write’ and press ‘Yes’ on the next prompt to continue

Once completed, select OK and Exit the Win32DiskImager

Checkpoint: Now, the SD card is called ‘boot’

**STEP 4**:  To remotely access the RaspberryPi, we need to enable SSH:

a.       Inside the ‘boot (drive:)’ (SD card) folder, create a Notepad (or any other text editor) file and leave it empty. Save the file name as: “ssh” and Save as type: ‘All Files’.

NOTE: It is important save the file name with the quotation mark, and include the quotation marks in File name. 

	Checkpoint: Inside the boot folder, you should see a file, named ‘ssh’, with no extension  

**STEP 5**: Eject the SD card, and insert it into your RaspberryPi

**STEP 6**: Connect an ethernet cable to RaspberryPi and lastly, plug in the power cable as well.

Once plugged in, LED lights are powered on RaspberryPi, and allow it to boot-up for about 1-2 minutes.

**STEP 7**: Open PuTTY software to access the RaspberryPi terminal – to make a secure connection you’ll need to know either hostname (which is set to ‘raspberrypi.local’ by default, if you have re-flashed your RaspberryPi’s operating system) or IP address of the RaspberryPi 

a.       On PuTTY configuration dialog box, under Host Name (or IP address) enter your hostname or IP address, and under Port, enter 22 (for SSH connection)

b.       Hit Open, and a command prompt will show up

c.       Inside the command prompt, enter ‘login as:’ and hit enter

d.       When prompted for password, enter the password and hit enter.

The default username is ‘pi’ and the password is ‘raspberry’. It is recommended that the user should change the password.

Congrats!!, you have developed an SSH connection with the RaspberryPi.

<br /><br /><br /> 

<u>Option #2</u>: Remote Desktop RaspberryPi (aka VNC)

This method will help you view the GUI interface of RaspberryPi on your laptop/PC by accessing the desktop screen of your RaspberryPi remotely

Software Requirement: 

\-          Download and install VNC Viewer using: <https://www.realvnc.com/en/connect/download/viewer/>

\-          You’ll need to know IP address of your RaspberryPi to access the desktop

\-          Connect your RaspberryPi to the internet and supply power to it.

**STEPS:**

**a.**       First, build an SSH connection with your RaspberryPi as mentioned in the previous method (using PuTTY software)

**b.**      Once logged into your RaspberryPi, in the command prompt, type ‘sudo raspi-config’ and hit enter

**c.**       Under the Raspberry Pi Software Configuration Tool (raspi-config), look for VNC Options (this could be under ‘advanced options’ or ‘interfacing options’ depending upon model of the RaspberryPi)

**d.**      Navigate to the VNC option and hit enter to enable it. (You may have to hit enter a couple of times) 

**e.**       Finally, exit the raspi-config menu through ‘Finish’ option. After this, you will be brought back to the command prompt again

**f.**        Now, reboot your RPi by typing ‘sudo reboot’ in the command prompt.

**g.**       Wait for it to reboot again, give it 1 -2 mins

**h.**      After a minute or two, open VNC viewer software and enter the hostname or ip address of your RaspberryPi

**i.**        This will log you into your RPi and the desktop screen will be displayed.

## Transfer files between your computer and RaspberryPi – in order to mirror an existing webserver

Requirement:

\-          Download and install FileZilla Client software using: <https://filezilla-project.org/>

Use the interface of this software to transfer files between your computer and RPi.

## Start InfluxDB on RPi:

**STEP 1**: In the command terminal of RPi, execute the following commands:

```sh
$ wget <https://dl.influxdata.com/influxdb/releases/influxdb-1.5.3_linux_amd64.tar.gz>

$ tar xvfz influxdb-1.5.3_linux_amd64.tar.gz	
```

NOTE: DO NOT INCLUDE $ SYMBOLS

***OR* STEP 1**: Install InfluxDB on RPi using ‘sudo apt-get install influxdb’ command in the RPi terminal

**STEP 2**: Execute the influxd file (on the terminal, type ‘influxd’) – This step helps make connection with the database. Leave this terminal running for as long as you want to stay connected with the database

**STEP 3**: Open a new terminal, run influx file (in the new terminal, type ‘influx’)

### TROUBLESHOOTING:

·         If you are unable to access the influx database, try adding repository keys by following the commands below (make sure to disconnect with the influx database)

```sh
$ curl -aL https://repos.influxdata.com/influxdb.key | sudo apt-key add –
$ echo "deb https://repos.influxdata.com/debian stretch stable" | sudo tee /etc/apt/sources.list.d/influxdb.list
$ sudo apt-get update
$ sudo apt-get install telegraf
$ sudo apt-get --reinstall install influxdb
$ sudo influxd
$ sudo influx
```

## Install Go Language on RPi:

In the RPi terminal, type the commands:

```sh
$ sudo apt-get install golang	
$ go build main.go
```

**ERROR? If upon executing ‘main.go’ file inside ‘webserver’ folder a gorilla/mux dependency missing error is shown, follow the next steps to fix the issue**:

<u>*Add GOPATH to the sudo root by following the commands*:</u>

```sh
$ mkdir ~/go
$ sudo bash
```

```shell
root@raspberrypi:/home/pi# env
root@raspberrypi:/home/pi# source ~/.bashrc
```

Last command will open .bashrc file, and inside this file, add the following two lines at the end of the file:

```powershell
export GOPATH=~/go

export PATH=$PATH:$GOPATH/bin
```

<u>Save and exit the file.</u>

```shell
root@raspberrypi:/home/pi# echo $GOPATH  
root@raspberrypi:/home/pi# go get -u github.com/gorilla/mux
root@raspberrypi:/home/pi# exit
```

At user@raspberrypi: terminal: -

\-          Navigate to the main.go file inside the webserver folder, and run the file:

```sh
$ go build main.go
```

**ERROR? Main.go: cannot find package "github.com/influxdata/influxdb1-client/v2", apply the following changes:**

```sh
~/Desktop/pi-server/webserver $ sudo bash

```

```shell
root@raspberrypi:/home/pi/Desktop/pi-server/webserver# source ~/.bashrc
root@raspberrypi:/home/pi/Desktop/pi-server/webserver# go get -u github.com/influxdata/influxdb1-client/v2
root@raspberrypi:/home/pi/Desktop/pi-server/webserver# go build main.go
root@raspberrypi:/home/pi/Desktop/pi-server/webserver# ./main

```

## Add data to InfluxDB:

Convenient method to add data to the database is using Postman software. Download and install Postman software (available for Linux, Windows and Mac).

Open Postman software and on builder page, select POST option from the drop-down menu. 

*DATA 1*:

Enter request URL: Fill in this section using syntax given on the next line:

http://localhost:###/sensor/info?id=32&name=first&coords=43.2585,-79.9201

Hit ‘Send’           (*NOTE: ### represents router number allocated in the main.go file for local development*)

*DATA 2*:

<http://localhost:###/sensor/data?id=32&measurement=Temperature&value=25>

Hit ‘Send’

Add more data points by changing the value listed at the end of the URL. For example, modify 25 to 5.

Now, whenever you insert a new value to the database, it can be viewed on the website just by refreshing the page.

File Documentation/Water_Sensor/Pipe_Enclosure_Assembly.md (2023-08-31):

# Pipe Enclosure Assembly

## Get hardwares

1. Pipe
	1. 3x6 Black ABS Pipe
	2. Permanent Cap
	3. Cleanout Adapter with Plug
	4. Pipe Connector
	5. ABS Cermet
	6. Gasket / Slicon
	7. 2lb Lead Weight
2. Electrics
	1. SMA Extender
	2. LTE/LoRa Antenna
3. Tools
	1. Drill
	2. Wrench

<details>
<summary>Parts photos</summary>
<br>

<b>Permanent Cap</b>

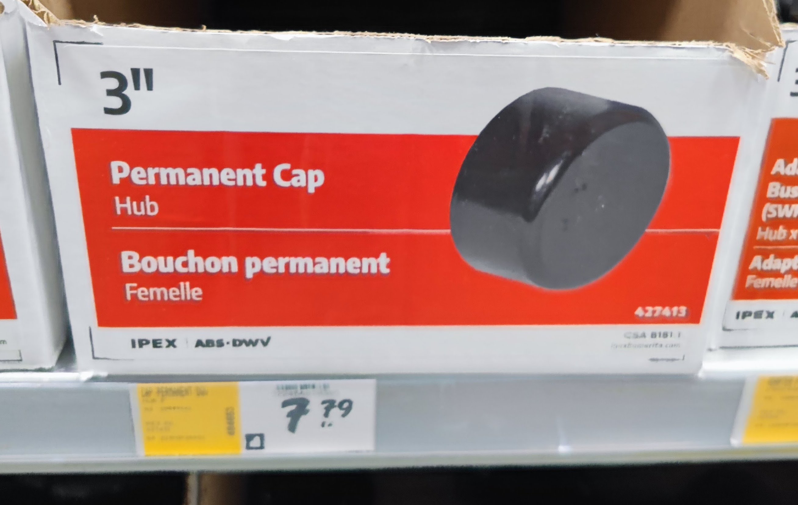
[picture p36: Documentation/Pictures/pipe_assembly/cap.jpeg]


<b>Cleanout Adapter with Plug</b>

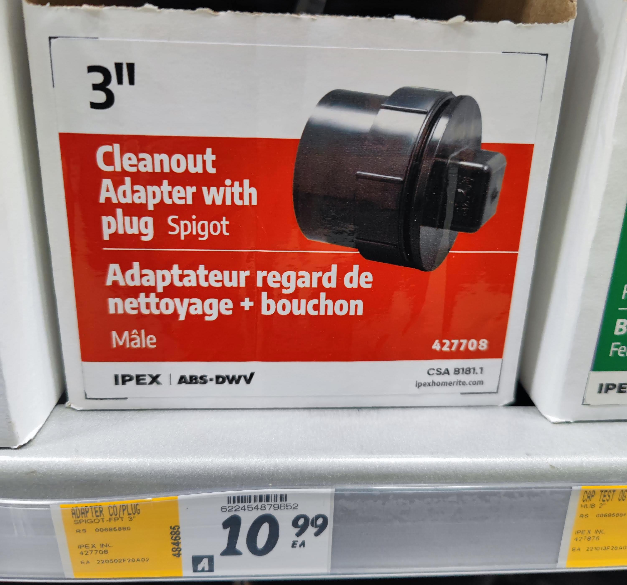
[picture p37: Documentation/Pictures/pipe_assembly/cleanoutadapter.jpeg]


<b>Pipe Connector</b>

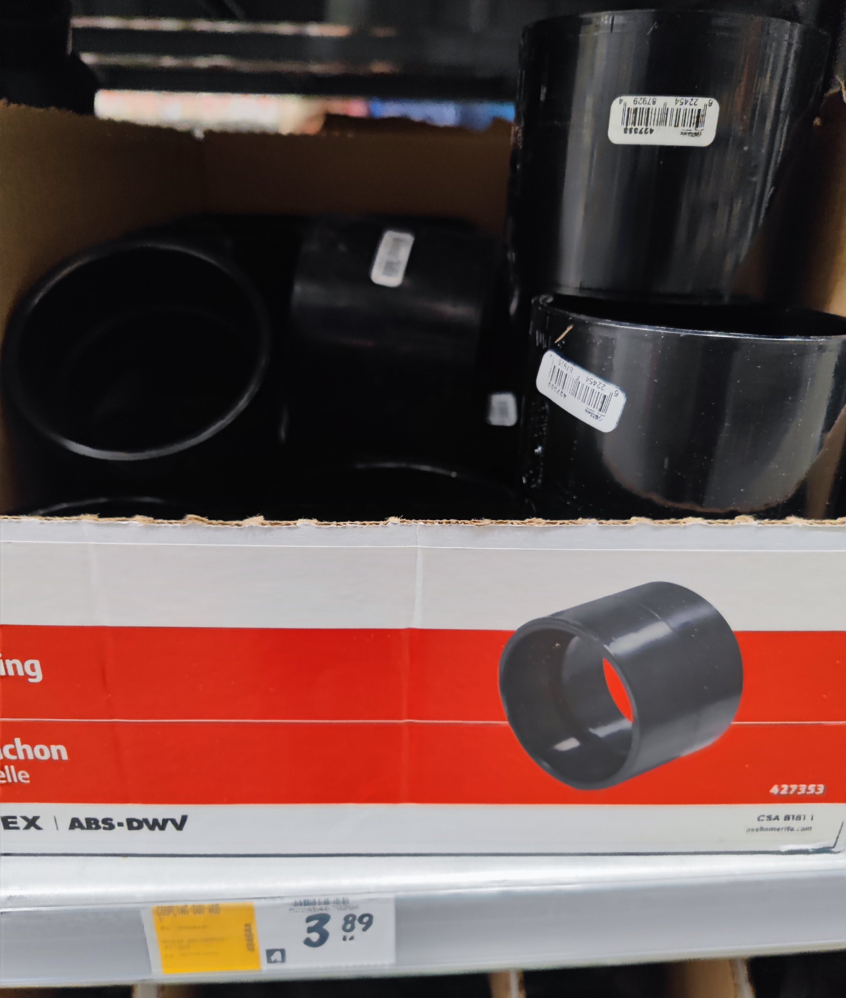
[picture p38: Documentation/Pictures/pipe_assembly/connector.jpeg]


<b>2lb Lead Weight</b>

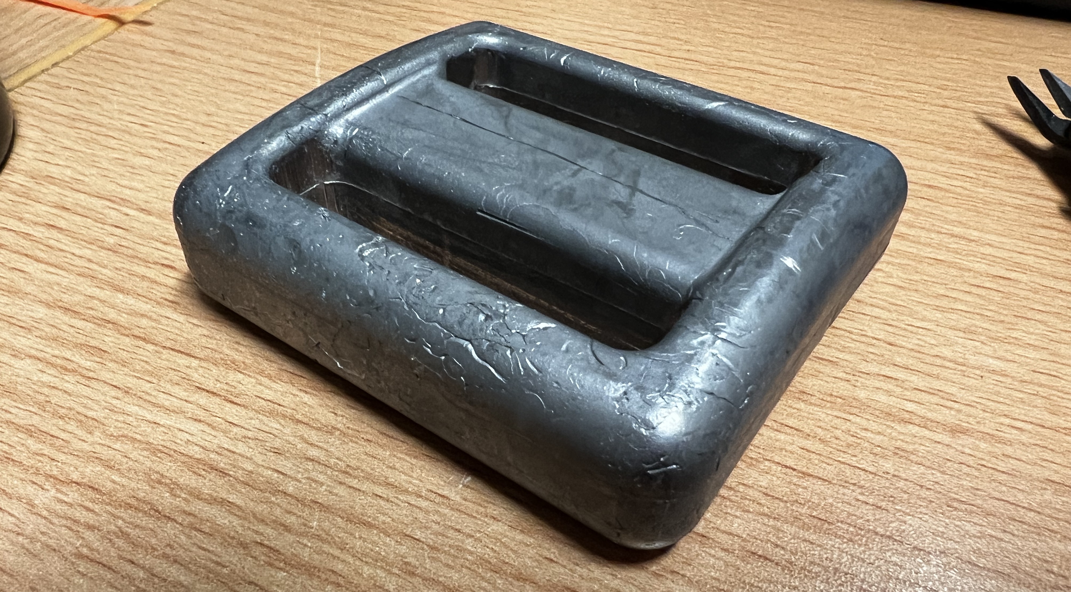
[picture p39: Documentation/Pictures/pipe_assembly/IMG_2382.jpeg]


</details>

## Pipe assembly

Cut an ABS pipe about 15 inches long.

Use cermet to seal the connecter between each connector using the following order:

	Cleanout Adapter with Plug
		->
	Pipe Connector
		->
	Black ABS Pipe
		->
	Permanent Cap



Using a drill to drill 4 holes in the clean-out adapter cap for sensor connector and antenna.

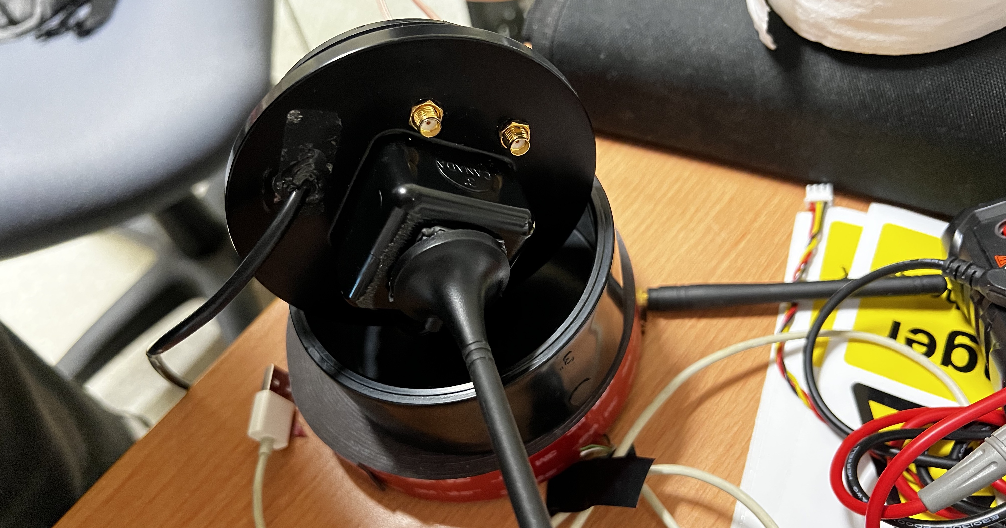
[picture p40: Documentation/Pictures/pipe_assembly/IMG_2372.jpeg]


Stick antenna at the top, let the cable go through one of the holes, and use gasket to waterproof the gap.

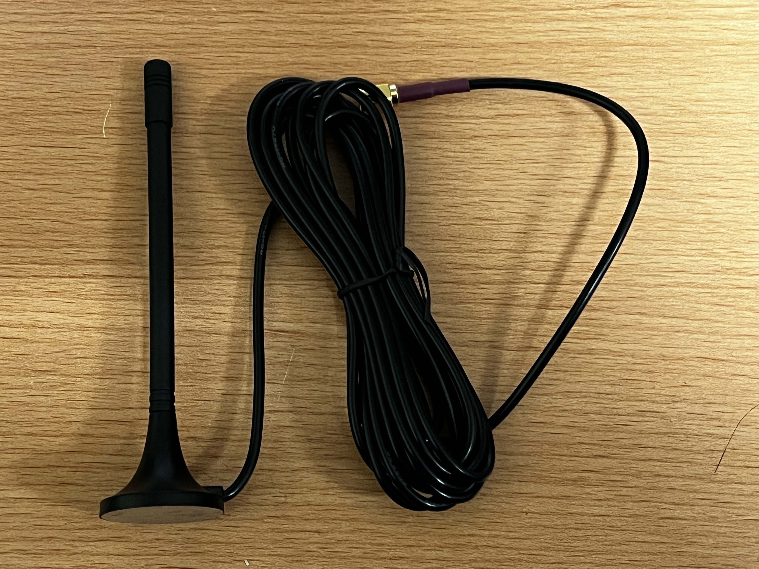
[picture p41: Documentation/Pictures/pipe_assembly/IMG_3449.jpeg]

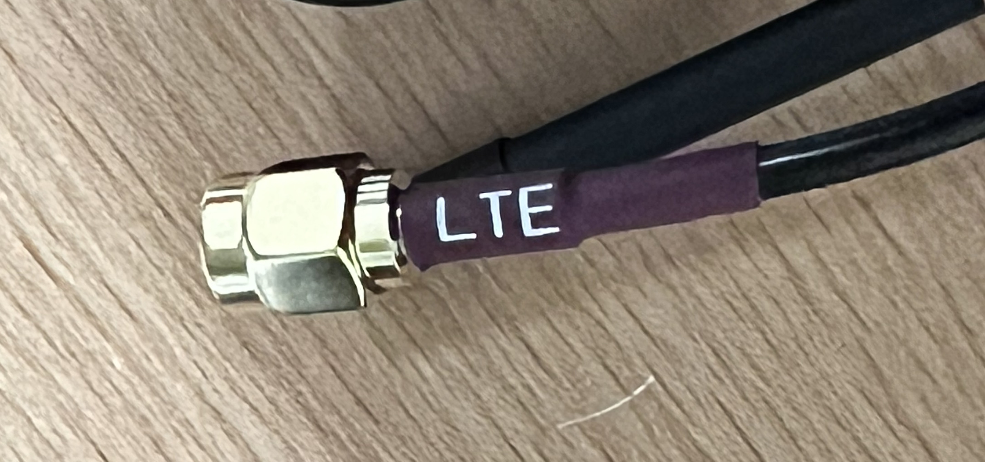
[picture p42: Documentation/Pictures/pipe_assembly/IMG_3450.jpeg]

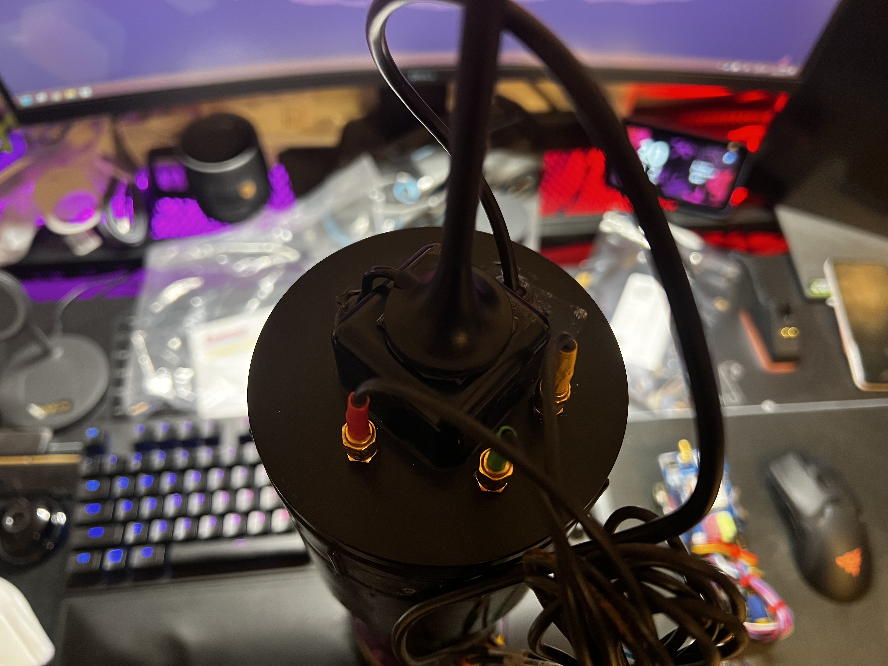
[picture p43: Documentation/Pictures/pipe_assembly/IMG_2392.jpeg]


Secure the SMA extender onto the holes and use a gasket inside the cap to make it waterproof.

Stick the lead weight in to the bottom (on the permanent cap).

## Check if the pipe is waterproofed and floated

Put a tissue paper inside the enclosure and submerge the pipe into a water tank, check if the paper is wet after some time.

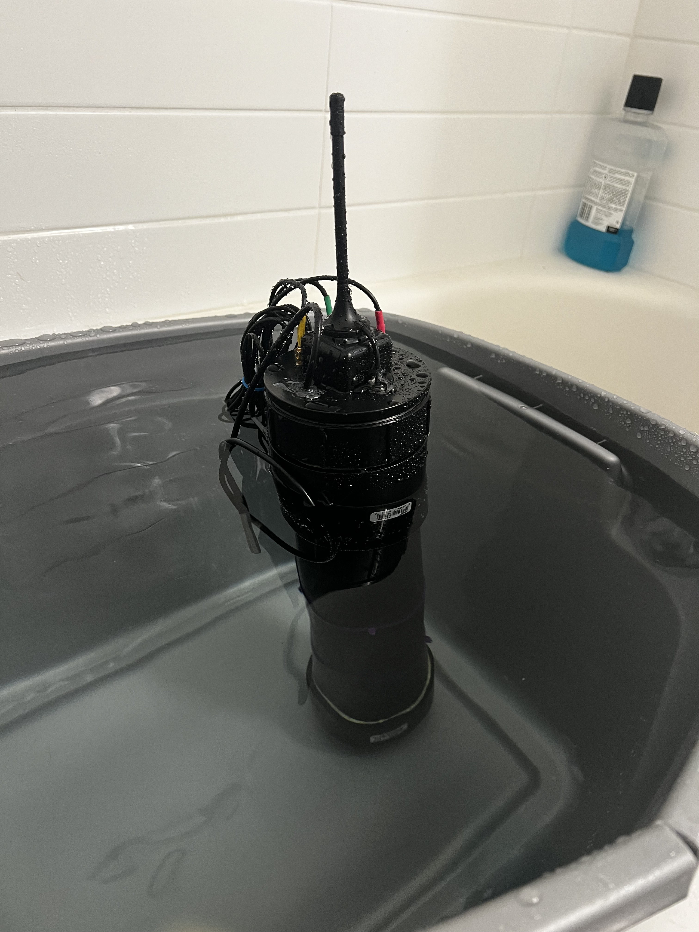
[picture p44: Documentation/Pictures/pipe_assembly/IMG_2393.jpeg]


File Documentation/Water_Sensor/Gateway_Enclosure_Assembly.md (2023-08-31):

# Build a Gateway Enclosure

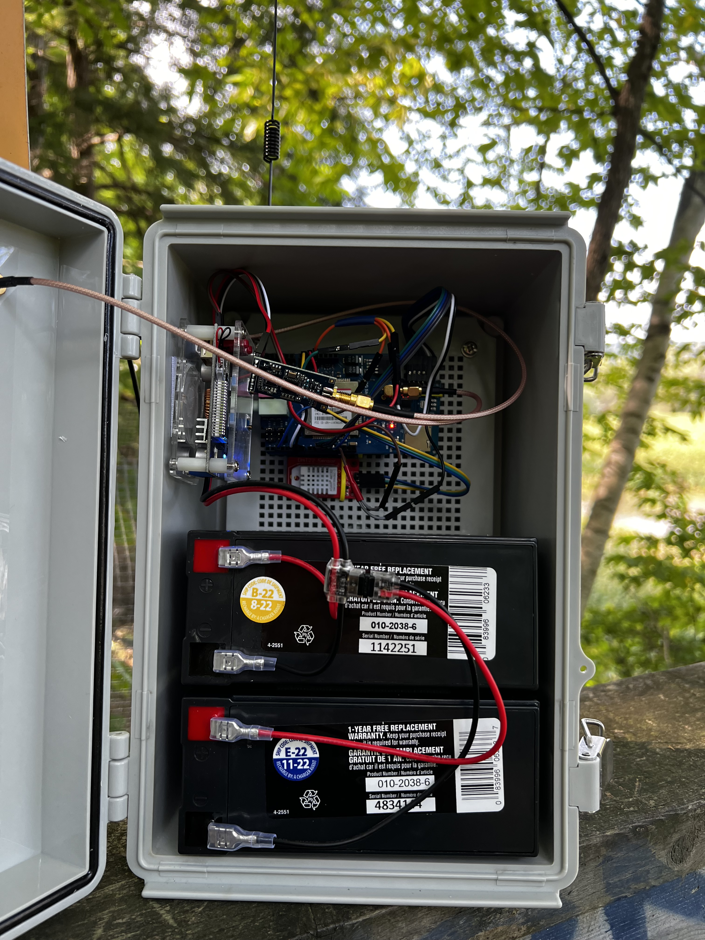
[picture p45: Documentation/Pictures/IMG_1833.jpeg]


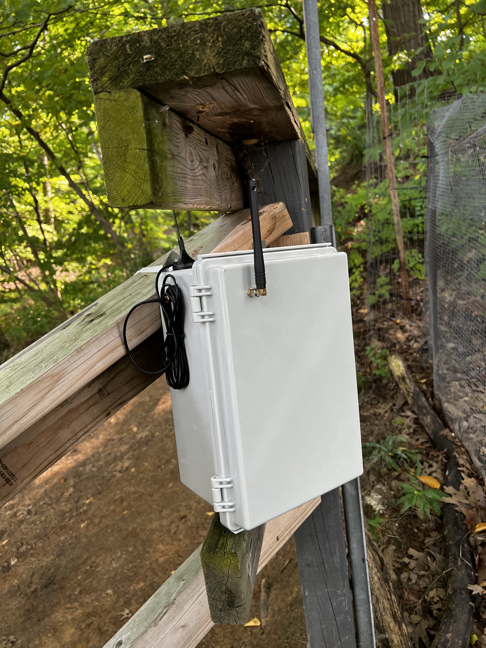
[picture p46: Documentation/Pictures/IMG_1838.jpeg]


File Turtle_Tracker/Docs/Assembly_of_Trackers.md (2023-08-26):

# Tracker Assembly

## Hardware Assembly

Cut GPS cable.

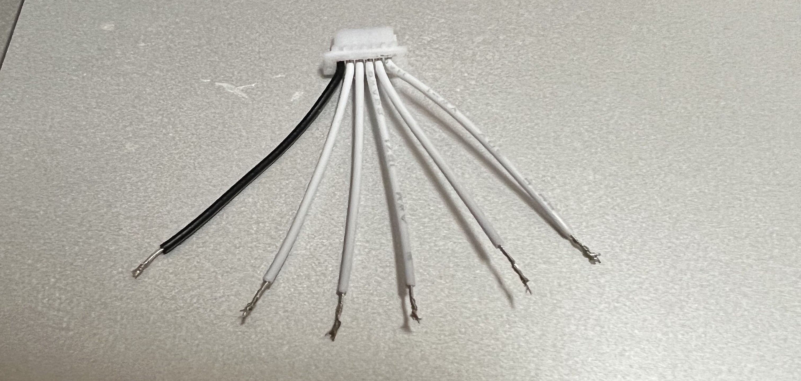
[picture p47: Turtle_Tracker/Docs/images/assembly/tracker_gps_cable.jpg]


Cut power cable.

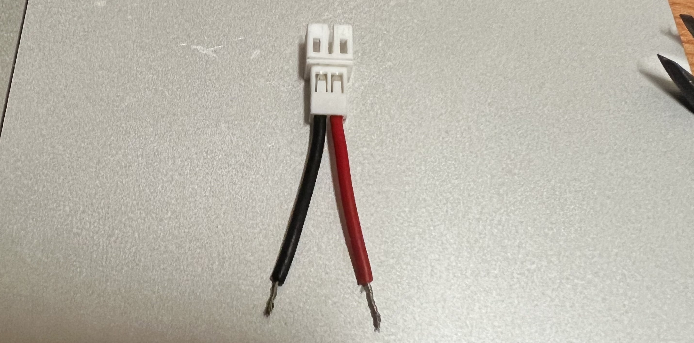
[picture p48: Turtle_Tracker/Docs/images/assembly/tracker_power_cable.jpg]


Get all parts ready.

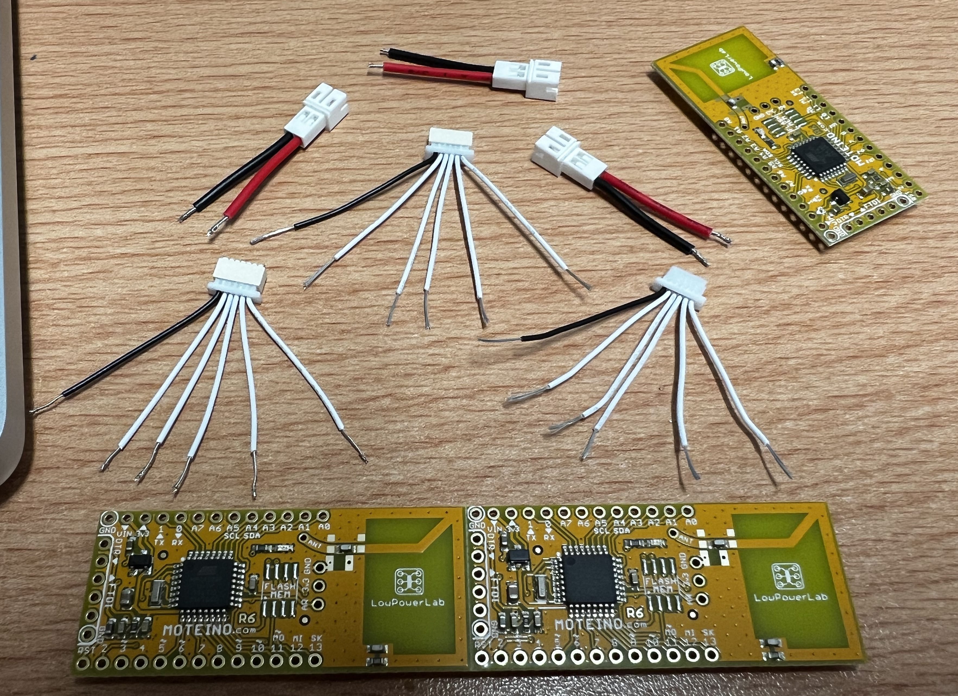
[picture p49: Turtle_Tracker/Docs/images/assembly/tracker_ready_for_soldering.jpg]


Connect the cable to moteino and solder in place.

**GPS ([Manual](./manual/GP-735T-150203.pdf)):**

- Connect GPS pin 6 to D6
- Connect GPS pin 4 to D4
- Connect GPS pin 3 to D3
- Connect GPS pin 2 to Vin / PWR
- Connect GPS pin 1 to Ground

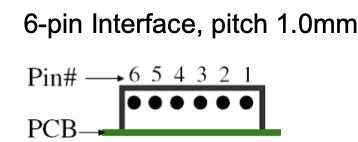
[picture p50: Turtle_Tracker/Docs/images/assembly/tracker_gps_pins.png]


Check with your battery if your battery has reversed Vcc and Ground, the power cable should also be reversed, in this case, the cable is reversed.

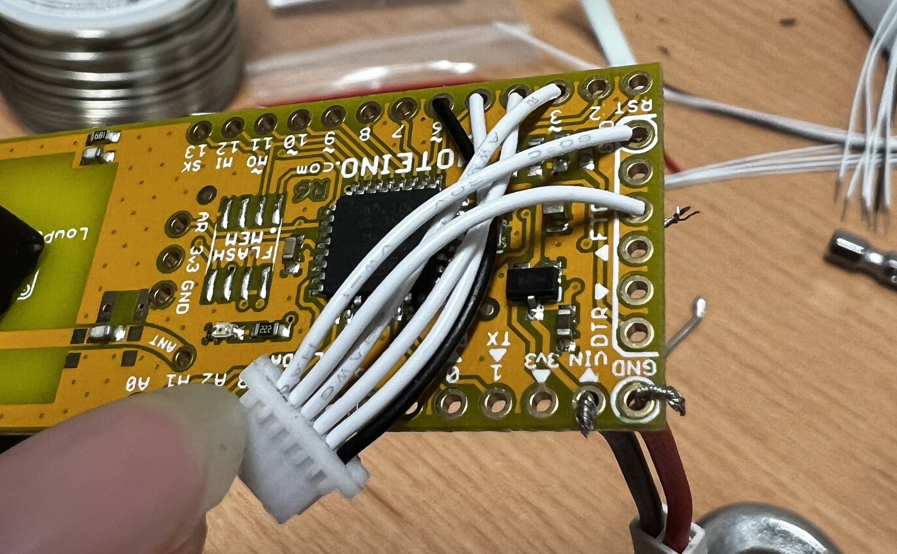
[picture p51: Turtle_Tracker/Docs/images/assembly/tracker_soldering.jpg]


## Flash firmware

Connect TX, RX, Reset, and power cable to moteino.

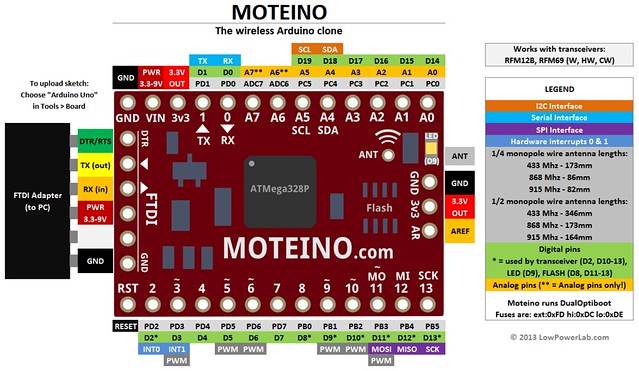
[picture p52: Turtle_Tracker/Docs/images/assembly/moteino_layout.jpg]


<br>

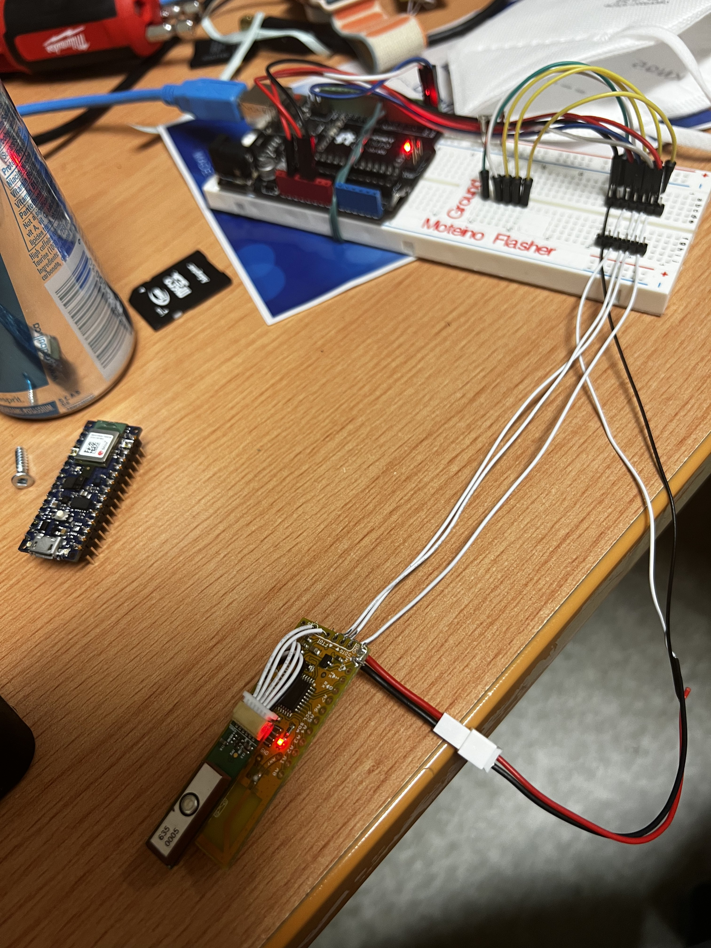
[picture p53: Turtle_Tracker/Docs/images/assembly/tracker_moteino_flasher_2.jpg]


Install the `Moteino AVR Boards` package in Arduino IDE: [Programming & Libraries](https://lowpowerlab.com/guide/moteino/programming-libraries/).

Move `../Arduino_Code/Library/libraries` to Arduino Library folder.

- Mac: ~/Documents/Arduino/libraries/
- Windows: /Users/{username}/Documents/Arduino/libraries/

Flash with Arduino IDE.

## Enclosure

3D Printed Tracker Enclosure: [Enclosure](./3D_Printed_Enclosure/README.md)

Spray `Plasti Dip` to make the 3D printing waterproof.

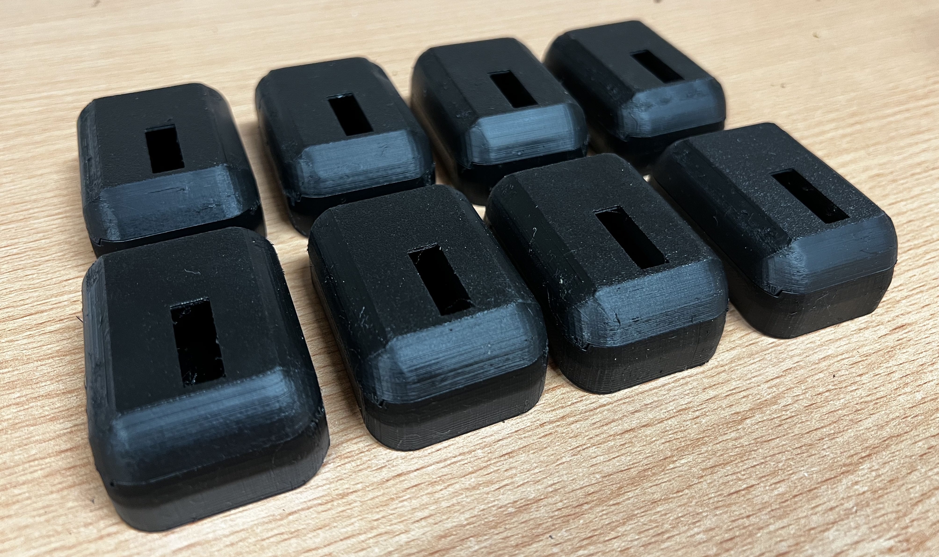
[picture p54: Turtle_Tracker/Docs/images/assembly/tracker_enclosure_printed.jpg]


Spray `Rust Aerosol Spray Paint` to make the screws not rusted.

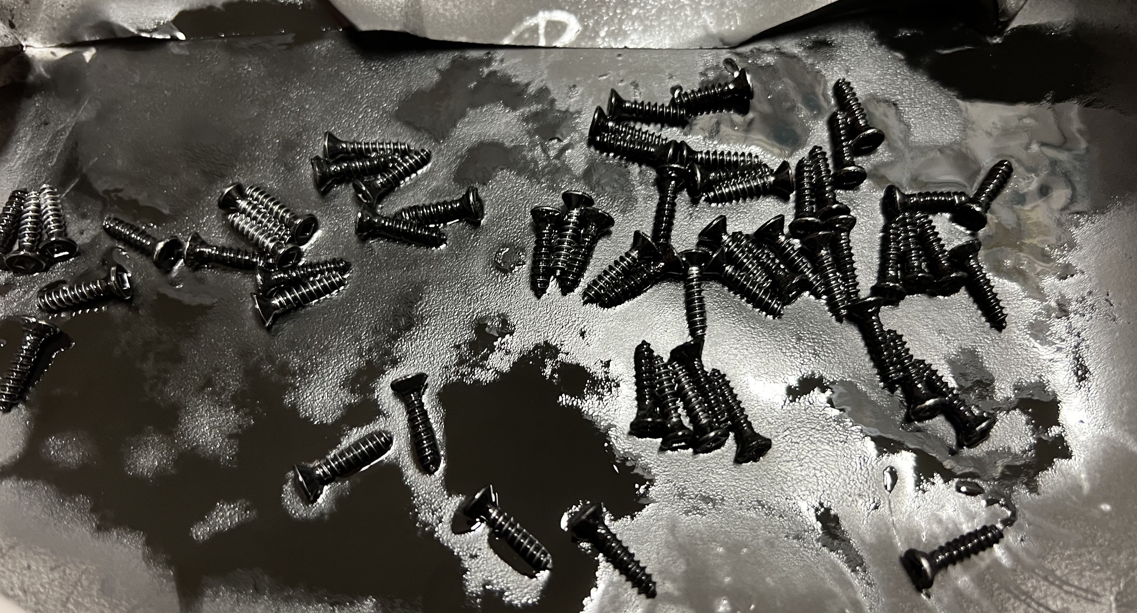
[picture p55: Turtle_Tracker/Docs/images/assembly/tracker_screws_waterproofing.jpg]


## Prepare to deploy:

Charge the batteries.

Caution: The 1600mAh Battery (currently using) Vcc and Gnd are reversed.

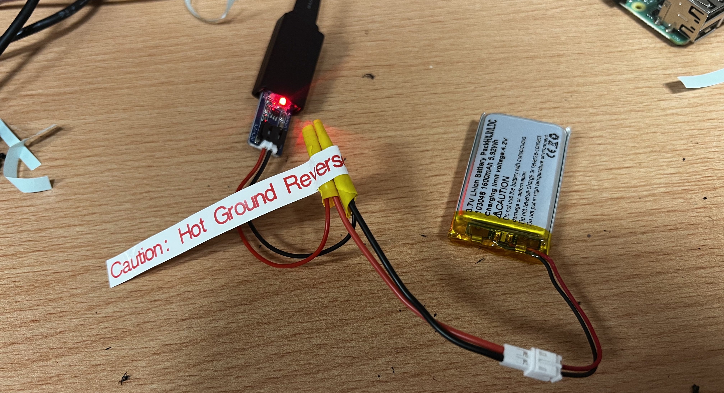
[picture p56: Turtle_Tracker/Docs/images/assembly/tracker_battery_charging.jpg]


Put the moteino and battery into the enclosure

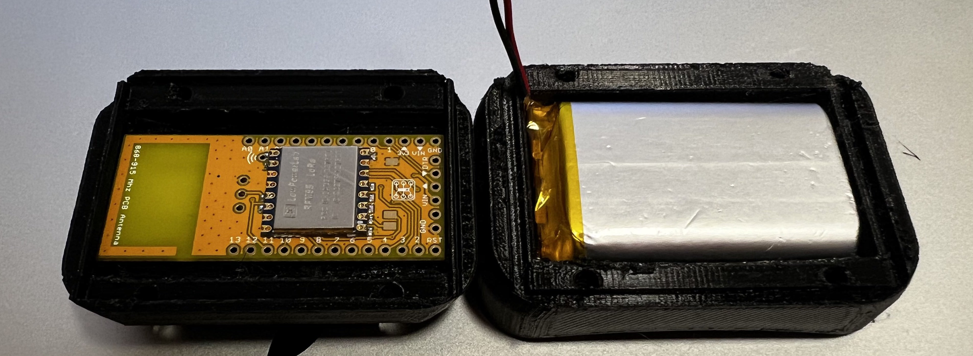
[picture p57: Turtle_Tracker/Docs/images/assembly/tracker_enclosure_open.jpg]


Seal the enclosure with a Gasket

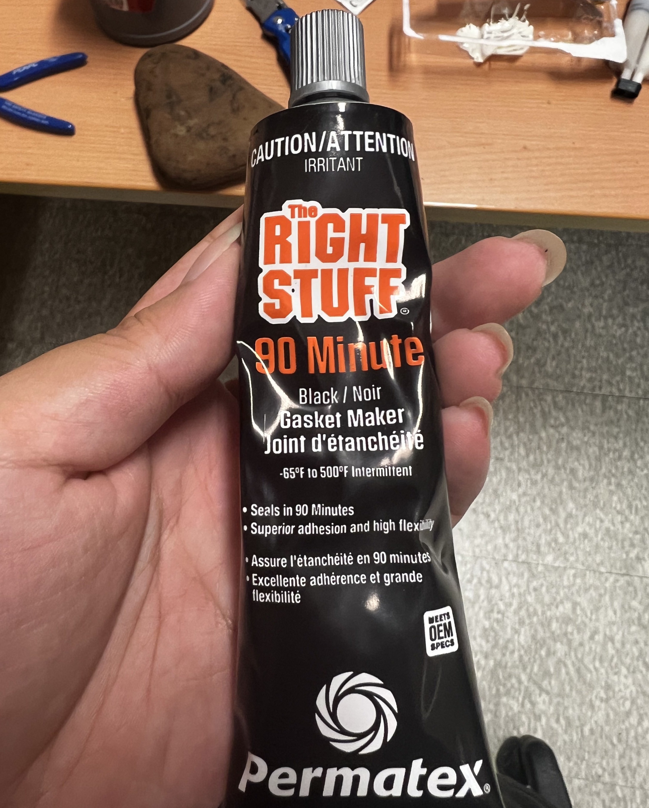
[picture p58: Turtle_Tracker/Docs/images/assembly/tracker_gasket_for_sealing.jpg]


Completed Trackers

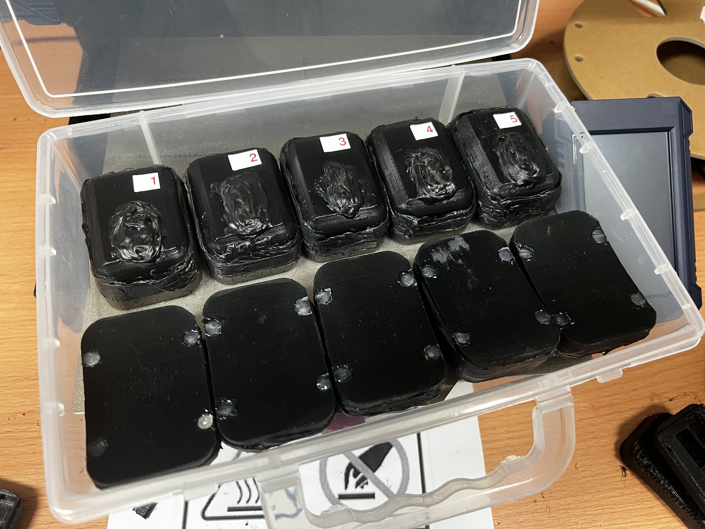
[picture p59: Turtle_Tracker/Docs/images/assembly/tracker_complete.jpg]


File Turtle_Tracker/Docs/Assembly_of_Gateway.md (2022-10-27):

# Gateway Assembly

## Hardware Assembly

(Gateway Image)

**LoRa Shield:**

- Attach LoRa shield to Arduino Uno

**Tinysine 3G Shield:**

- Bend pin 8 and connect to A1
- Bend pin 9 and connect to A0
- Attach 3G shield to Arduino Uno
- Connect Tx to Arduino D4
- Connect Rx to Arduino D5

(Bended pin image)

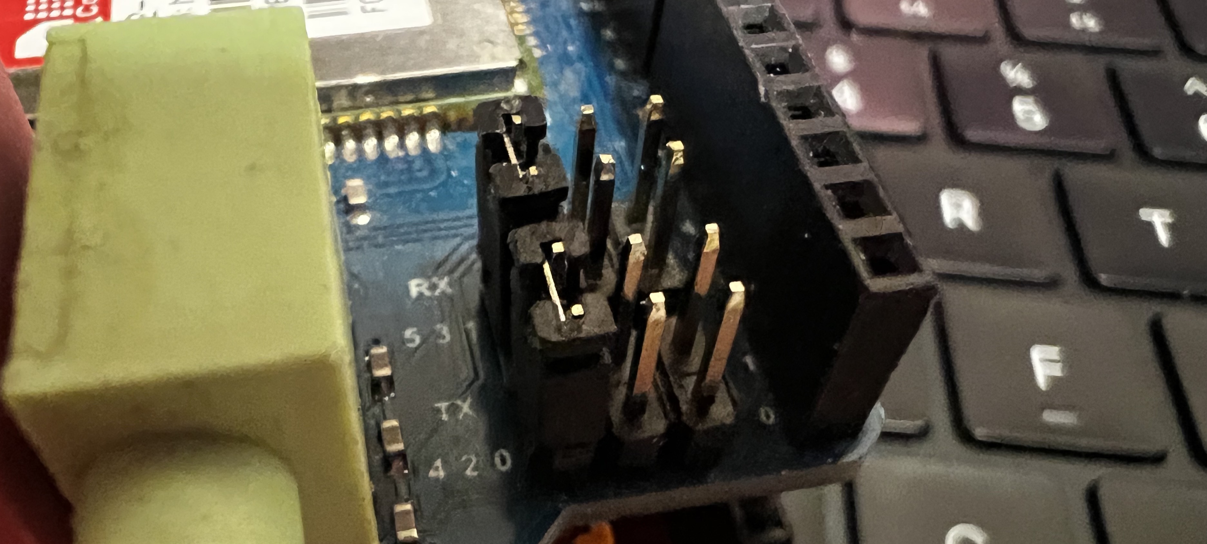
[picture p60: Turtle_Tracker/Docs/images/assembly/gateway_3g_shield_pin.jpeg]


**SD Card:**

- Connect `MISO` Pin to A2
- Connect `MOSI` Pin to A3
- Connect `SCK` Pin to A4
- Connect `CS` Pin to A5
- Connect Vcc Pin to Vcc
- Connect Ground Pin to Ground

## Configure Tinysine 3G Shield

[3G Shield Set Baud](./3g_shield_setbaud/README.md)

## Flash firmware

Move `../Arduino_Code/Library/libraries` to Arduino Library folder

- Mac: ~/Documents/Arduino/libraries/
- Windows: /Users/{username}/Documents/Arduino/libraries/

Flash with Arduino IDE

## Enclosure

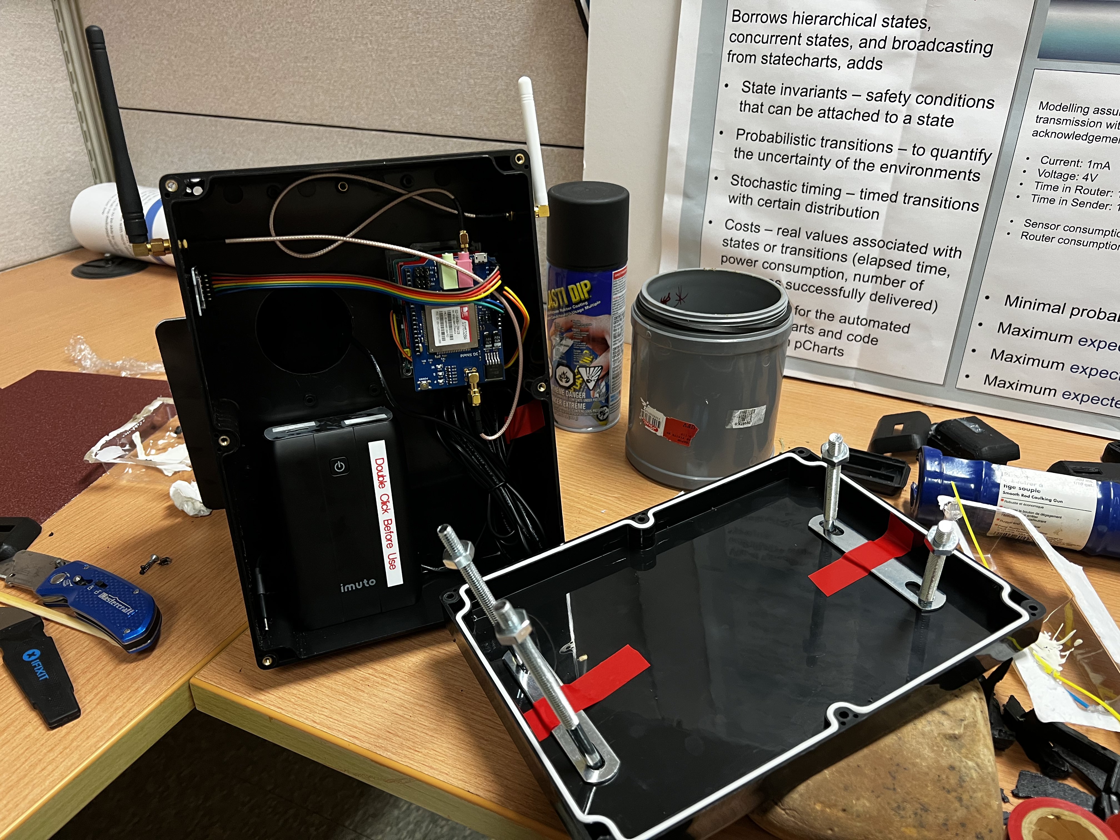
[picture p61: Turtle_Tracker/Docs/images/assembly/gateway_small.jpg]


<br>

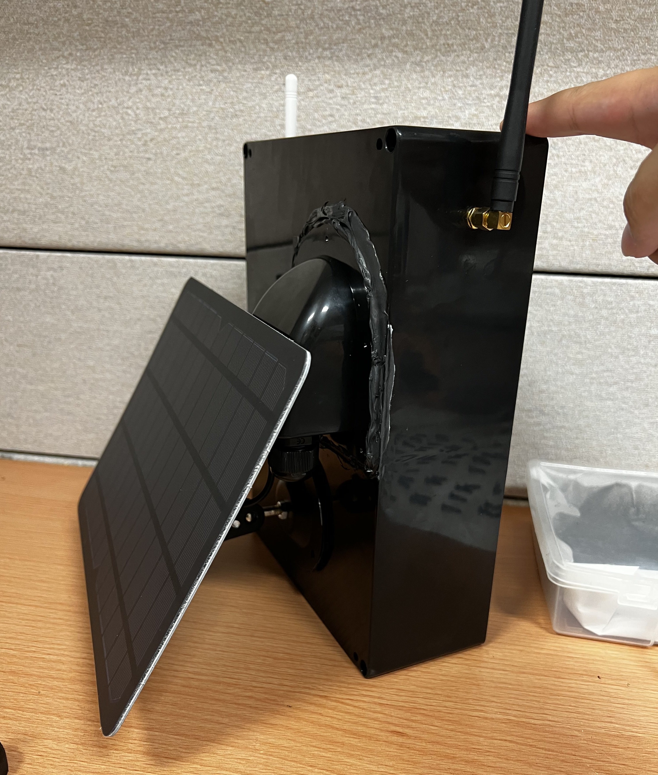
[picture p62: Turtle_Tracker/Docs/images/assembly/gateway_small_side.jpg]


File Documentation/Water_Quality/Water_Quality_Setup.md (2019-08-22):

# Setting Up This Project

This file describes how to get this setup working properly, from the hardware to the software.

# Setting up the server

To setup a custom server on a [Raspberry Pi](https://www.buyapi.ca/product/raspberry-pi-4-model-b-1gb/), follow the instructions found [here](https://gitlab.cas.mcmaster.ca/re-mote/pi-server/blob/master/Documentation/RaspberryPi_Instructions.md).

For instruction on using a cloud service, look [here](https://gitlab.cas.mcmaster.ca/re-mote/publications/tree/master/HuangMengqi19Encryption&Storage).

# What You Need

## The Hardware You Need

What you'll need will of course depend on what kind of setup you're trying to achieve.

### Gateway

For each Gateway, you'll need:

* One Arduino compatible micro controller. At least 32 kB of flash memory and 2kB of ram is highly recomended, although more is prefered. The [Arduino Uno](https://store.arduino.cc/usa/arduino-uno-rev3) seems to work well
* A 3G module of some sort. The current two supported are the [Tinysine 3G shield](https://www.tinyosshop.com/3g-gprs-gsm-shield-for-arduino-sim5320a) and the [Adafruit FONA 3G](https://www.adafruit.com/product/3147)
* A sim card with a data plan on it. Where to get this sim card will heavily depend on where you are
* A [LoRa mesh module](https://www.dfrobot.com/product-1670.html)
* A [microSD card module](https://www.amazon.ca/Senmod-Adapter-Reader-Module-Arduino/dp/B07GXBP672)
* A [microSD card](https://www.amazon.ca/SanDisk-Ultra-microSDXC-Adapter-SDSQUAR-128G-GN6MA/dp/B073K14CVB). It's recomended that it is at least 1GB, a breakdown of size to data points can be found in the [Data Storage Options file](https://gitlab.cas.mcmaster.ca/re-mote/publications/blob/master/VictorVezina19MeasurementDataStorage/Data_Storage_Options.md)
* Any sensors you want to connect to it, see the [sensor options section](#sensor-options) for more information
* An appropriate power option, see the [power options section](#power-options) for more information
* Some form of [eclosure](#enclosures)

As with everything in the setup, these parts could be changed out for others (ex: changing data storage, using a different 3G module, etc), the listed options are simply what is currently supported.

### End node

For each End node, you'll need:

* One Arduino compatible micro controller. At least 30kB of flash memory and 1.5kB of ram is highly recomended. The [Arduino Nano](https://store.arduino.cc/usa/arduino-nano) seems to work well
* A [LoRa mesh module](https://www.dfrobot.com/product-1670.html)
* A GPS module of some sort. The [GP-735](https://www.sparkfun.com/products/13670) is very good, although expensive
* Any sensors you want to connect to it, see the [sensor options section](#sensor-options) for more information
* An appropriate power option, see the [power options section](#power-options) for more information
* Some form of [eclosure](#enclosures)

Once again, these parts could be changed out for others, the listed options are simply what is currently supported.

### Sensor options

There are quite a few currently supported sensors, including some for water and air quality. The list is as follows:

* [Atlas Scientific Dissolved Oxygen Sensor](https://www.atlas-scientific.com/product_pages/kits/do_kit.html)
* [Atlas Scientific Conductivity Sensor](https://www.atlas-scientific.com/product_pages/kits/ec_k1_0_kit.html)
* [Atlas Scientific pH Sensor](https://www.atlas-scientific.com/product_pages/kits/ph-kit.html)
* [DFRobot Gravity Analog Turbidity Sensor](https://www.dfrobot.com/product-1394.html)
* [DFRobot Gravity Waterproof DS18B20 Sensor (Temperature)](https://www.dfrobot.com/product-1354.html)
* [DHT22 sensor (Air Temperature and Humidity)](https://www.amazon.ca/gp/product/B07CM2VLBK/)

A couple caveats: 

* When using any two (or more) Atlas Scientific sensors together, any Conductivity and pH sensors should use a [voltage isolator](https://www.atlas-scientific.com/product_pages/circuits/basic-ezo.html). A caveat to the caveat: when using a pH and Conductivity sensor together, only the pH sensor needs to be isolated. Read the EZO data sheets provided by [Atlas Scientific](https://www.atlas-scientific.com/) for more information.
* The software is currently setup to where if you are using pH or Conductivity sensors, multiple sensors of the same type must either all be isolated or all not isolated (this should be respected through the first caveat anyway)
* Using multiple sensors on the Gateway may cause flash issues. If you plan on using lots of sensors on the Gateway, get a micro controller with enough flash (64kB+)
* The DHT22 sensor is not weather proof, so you must make sure that your enclosure accounts for this

You can also use your own sensors with this system, instructions on how to do this can be found [here](Custom_Sensors.md).

### Power options

Details on power consumption of [End-Node](../Power%20Consumption%20Analysis%20of%20Nodes/End-Node_POWER_CONSUMPTION.md) and [Gateway-Node](../Power%20Consumption%20Analysis%20of%20Nodes/Gateway_Node_POWER_CONSUMPTION.md).

### Enclosures

Check out the details of [solar panel](../Enclosure%20-%203D%20Printing%20Model/Solar%20Power%20Enclosure), [end-node](../Enclosure%20-%203D%20Printing%20Model/End%20Node) and [gateway-node](../Enclosure%20-%203D%20Printing%20Model/Gateway%20Node) housing units. Download .stl files [here](../Enclosure%20-%203D%20Printing%20Model/STL%20Files).

## The Software You Need

### Arduino IDE

First, you'll need the [Arduino IDE](https://www.arduino.cc/en/main/software). This will be used to upload the code from your computer to the Arduino compatible micro controller. If you want, you could also use the Arduino web editor, or any other IDE that supports uploading .ino files to Arduinos.

### Program file

Next, you'll need to download [Node_Code.ino](../../Node_Code/Node_Code.ino) from this repository. This is the main program that runs on the Arduino.

### Libraries

You'll then need to download the libraries from this repository, and add some others from the IDE. First, copy all files found under [Libraries](../../Libraries/Libraries_Victor) into your [Arduino library folder](https://www.arduino.cc/en/guide/libraries), replacing what's already there (if anything). You'll then need to install these other libraries using the IDE's built-in library manager:

* DHT_sensor_library
* NeoGPS
* OneWire
* SdFat

If you wish to run the program in "debug mode", you'll need to download the [MemoryFree library](https://github.com/maniacbug/MemoryFree).

<br>  

# Assembling the Hardware

## Gateway

## End node

<br>  

# Configuring and Uploading the Software

## Gateway and End Node

The main configuration file, remoteConfig.h, can be found under the re-moteConfig library file. This is the only file you need to change to configure the Arduinos (assuming you aren't adding custom support). You need to comment and uncomment out lines 15 and 16 depending on if you're uploading to a Gateway or an End node. You then need to change the rest of the settings in that file to accomodate for your particular setup. The settings in the file all have clear comments that explain what that setting does.

<br>  

# Testing

It's important to test your setup at every stage of this document to make sure everything is functioning correctly. It is also highly recommended that once everything is finished, you run a full test over the course of a few days. This will ensure that everything is functioning as expected. If at some stage in the setup proccess something does not work, please refer to the [Troubleshooting section](#troubleshooting).

<br>  

# Deploying

Once everything is completely ready to be deployed, it is important to deploy them correctly. The first step is to choose your deployment location carefully. The LoRa mesh modules used allow for your nodes to be set up in a mesh configuration, which means that as long as a node (node 1) is within range of any other node (node2) that is connected to a gateway, the first node (node 1) will be able to connect to the gateway. This allows for a long string of end nodes connected to each other and only one gateway. The tested range of these LoRa mesh modules is about 200m through heavy obstruction (hill, buildings, etc.), about 500m through light obstruction (trees, etc.), and 650m through very light obstruction (chain link fences, nothing, etc.). This range can be improved by lifting the antenna, but by how much depends heavily on your circumstances (tested up to about +100m). It is also important to consider the legality of your deployment locations; you must ensure that you are not breaking any laws by deploying your nodes in the locations.

The next thing to consider when deploying your nodes is hardware safety. It is important to make sure that your nodes will not be dislodged or washed array by heavy rains, strong winds, or snow (depending on the weather where you're deploying). Depending on your deployment locations, it may also be important to consider hiding/securing your nodes in some way to prevent vandalism. This could be done by burying your nodes (although this may affect GPS and LoRa connectivity), painting them to blend in, or covering them with something (could be leaves, or even trash, etc.).

Once the nodes have been secured, it is important to deploy the sensors so that they are secure. For us, this involved putting a large steel pole into the water, and securing the sensor probes to it using water proof tape. The steps to do this will depend on the location and sensor probes you are using.

<br>  

# Using the website

To use your website, either enter the IP address of your personal server into a web browser (for your own server), or go to the website that hosts your website (for a cloud service). You may need to add a /# after the IP/URL. Once there, you should be able to see a map with the locations of all the nodes you have setup. To select a node, click on its pin on the map or select it from the Location drop-down menu. You can then select the measurement you wish to see the data for in the Sensor Type drop-down menu. Sensor Types in black are available at that node, Sensor Types in gray are not.

To see a list of nodes that contain a certain measurement, first unselect a location from the Location drop-down menu, then select the measurement you wish to use. When you expand the Location drop-down menu, the locations in black contain that measurement, and the locations in gray do not.   You may also notice that when you have a location selected, it will create a path with circles on the map. Each circle represents GPS co-ordinates where that node was located.

Once you have both a Location and Sensor Type selected, a table containing the date, time, and value of every data point will appear under the map. Underneath the table you will see a graph representing the sensor data through time.

<br>  

# Troubleshooting

The first step to troubleshooting is to make sure you've configured and connected everything correctly. If that didn't help, the next step is to identify the problem. This is most easily done by isolating parts of the Arduino and seeing which ones function correctly and which ones do not. If you've been testing after every step of this document, this should be quite easy. Once you've isolated the problem (let's say your DO sensor isnt initialising), it is good practice to re-check the configuration for this module to make sure that isn't the cause of the problem. If that wasn't the problem, you then need to determine if the problem is with the module or the Arduino. This is most easily done if you have another Arduino or sensor to swap in. If not, you can try to change the pins the sensor is connected to (ideally to pins you know work). If the problem is with the sensor, you may have gotten a defective one and will have to contact the seller. If the issue is with the Arduino, you can try changing the pins the sensor is connected to to see if some of the pins are broken. If that doesn't help, try testing the Arduino with a simple LED blink sketch. If the module and Arduino work seperately, but not together, you will have to do proper software bug finding and fixing, for which it is recommended that you have some form of experience with software development, preferrably in Arduino or C/C++.

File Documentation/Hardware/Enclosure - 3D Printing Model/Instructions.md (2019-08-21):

STEP#1:
Once you download the .ipt files for a box, please open and convert them into .stl files using Autodesk Inventor software. 

OR

Download the .stl files from the STL folder.

STEP#2:
Download and install the slicer software (preferably, follow the link: https://www.prusa3d.com/drivers/  - PrusaSlicer
OR 
download any of the other slicing softwares, such as Cura
OR
if you know the type of your 3D printer, perhaps check their online website - most likely, the 3D printer company provides a slicing software for free)

STEP#3:
Open .stl files in the slicer software, and re-arrange the items on the virtual bed in order to keep them within the boundaries (most slicers have the option to self-arrange and self-orient the parts while keeping the run-time at minimum).

STEP#4:
Adjust the print settings according to your needs (or you can use the default settings). Please change a few parameters to see how it affects the run-time, for example, in the 'Print Settings' option, if you select the finest bead size, it would increase the print time. 
- Select the right filament type and printer type
- Recommended to enable the Support and Brim option 
- Keep the scale factor at 100% to print correctly sized parts 

STEP#5:
After setting and verifying all the options available to you, hit Slice button. This would generate a G-code for the 3D printer and calculate the amount of time to finish the job.
- Export the G-code in a folder (or, directly into an SD card)

STEP#6:
Insert the SD card in the printer SD card slot. Find the G-code file name from the list, and hit the print button. 
- Make sure to clean the printer's bed with isopropyl alcohol/cleaning agent
- Suggestion: After selecting the right file name, let the printer run for the first layer and inspect that the material is sticking to the bed. If not, clean the bed or use a sticking solution, or adjust the z-axis.

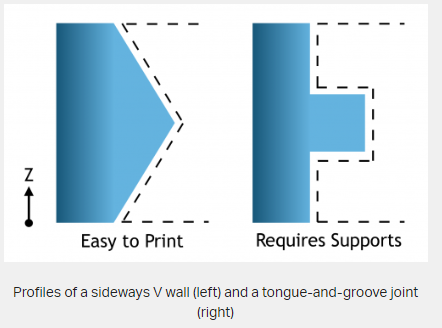
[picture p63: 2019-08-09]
Research/Ryan_Notes/Images/Joints/Sliding-Joint-Printing.PNG

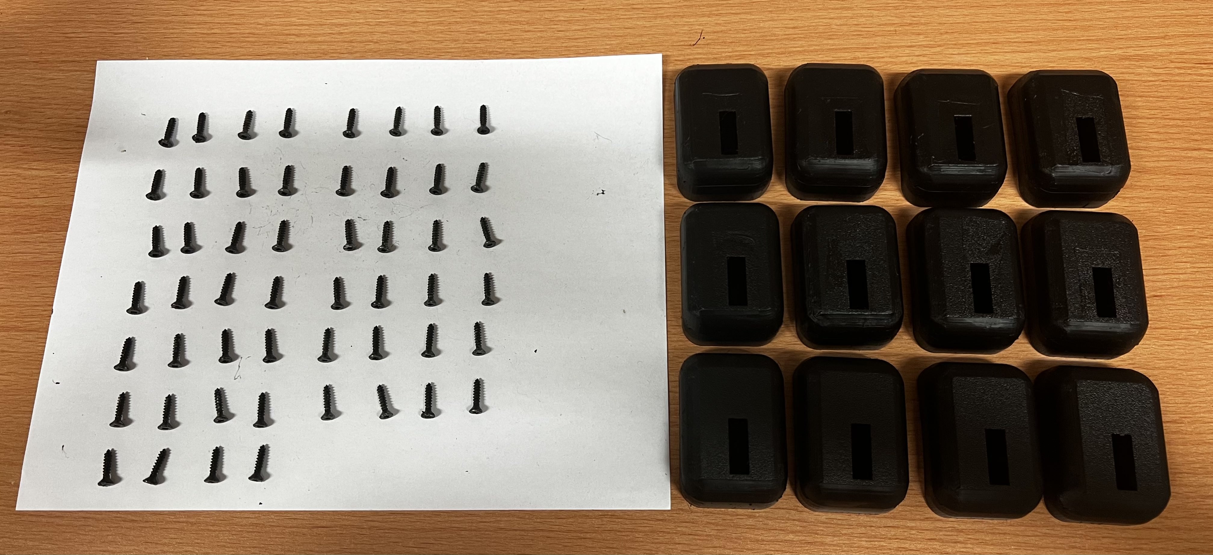
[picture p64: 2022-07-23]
Turtle_Tracker/Docs/images/assembly/tracker_enclosure_ready.jpg

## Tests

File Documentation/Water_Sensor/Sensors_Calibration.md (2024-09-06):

# Sensors Calibration through Web Serial

Ensure that all sensors are attached properly and that room temperature is around 25 degrees.

Open the calibration website at `https://{your-server-ip}/configuration` (replace your-server-ip to your own server IP) on Chrome or a web browser with USB web serial supported (Public website: https://macwater.cas.mcmaster.ca/configuration/).

Press `F12` to open the development tool and navigate to the `Console` tab.

Connect the Arduino board to your computer using USB.

Click `Connect` and select the device.

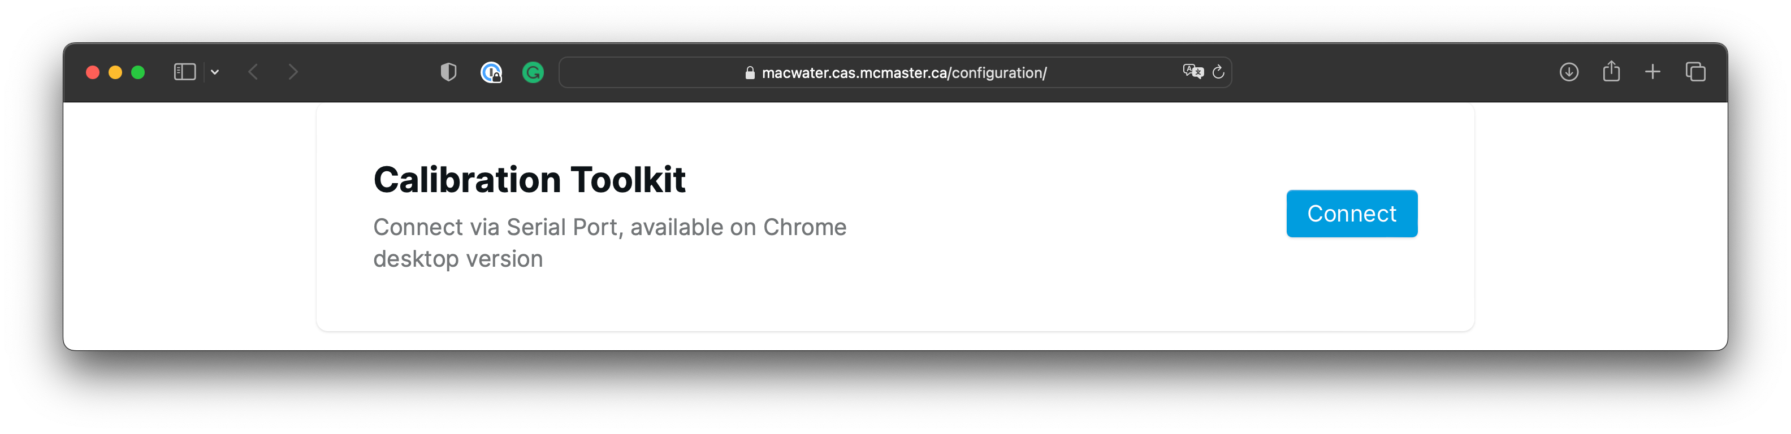
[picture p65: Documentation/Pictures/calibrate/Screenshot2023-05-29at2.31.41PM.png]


### Supported Sensors

- Atlas Scienticfic pH Sensor
- Atlas Scienticfic EC Sensor
- Atlas Scienticfic DO Sensor

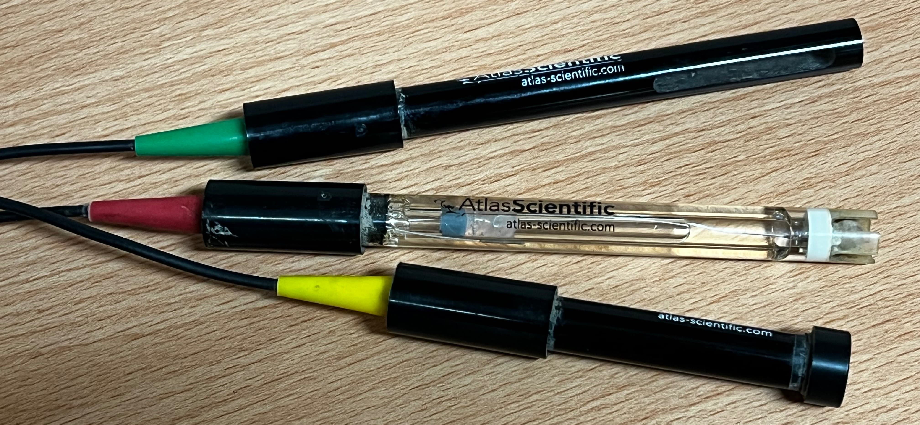
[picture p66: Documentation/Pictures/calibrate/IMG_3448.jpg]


## pH Sensor Calibration

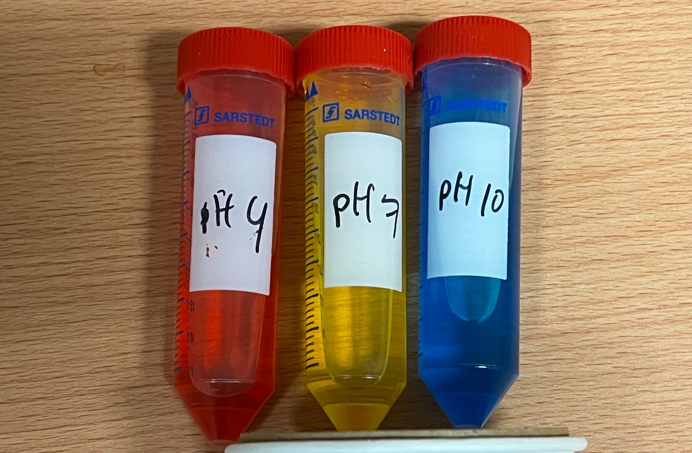
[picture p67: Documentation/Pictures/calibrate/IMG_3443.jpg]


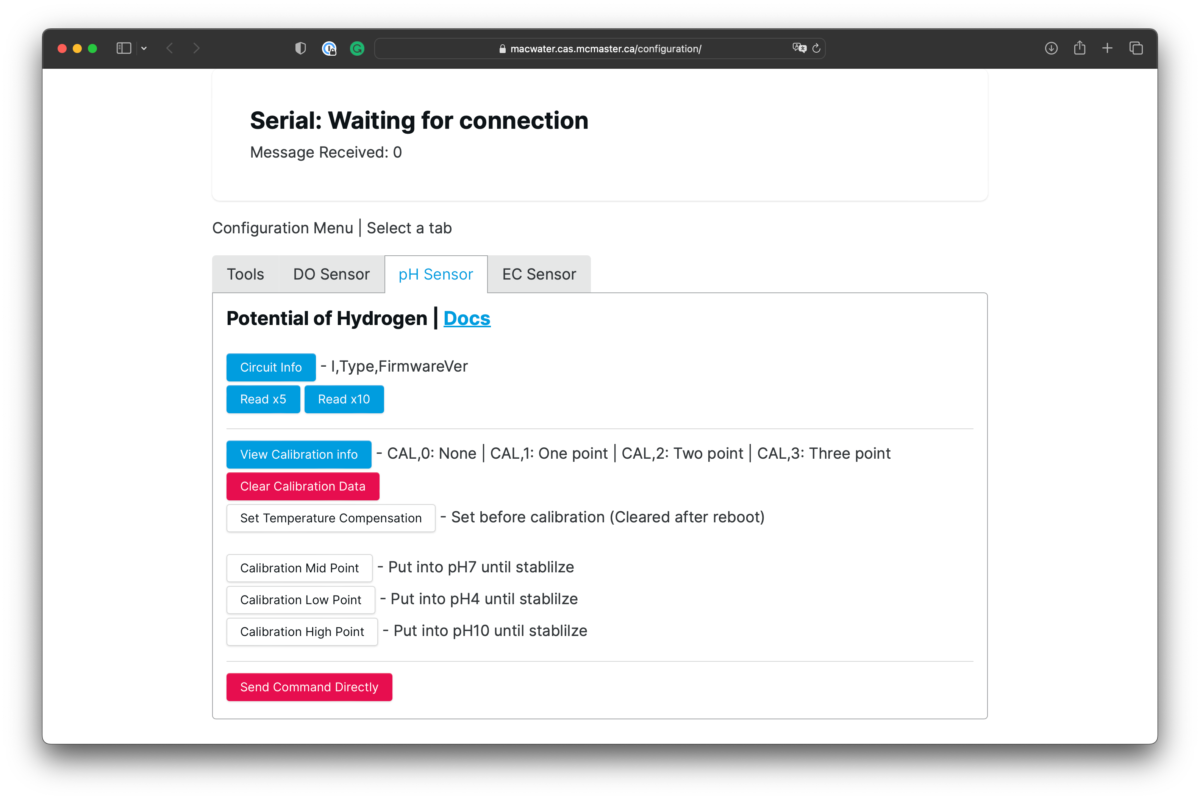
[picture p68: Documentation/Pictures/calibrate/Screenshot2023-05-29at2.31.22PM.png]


Place the pH sensor in the pH7 calibration liquid, using the `read x10` button to check that the reading is stable.

After the reading is stable, press `calibration mid-point`.

Place the pH sensor in the pH4 calibration liquid, using the `read x10` button to check that the reading is stable.

After the reading is stable, press `Calibration Low Point`.

Place the pH sensor in the pH10 calibration liquid, using the `read x10` button to check that the reading is stable.

After the reading is stable, press `Calibration High Point`.

Press the `View Calibration Info` button, and make sure the reading is `cal, 3` (3 Point Calibration).

## EC Sensor Calibration

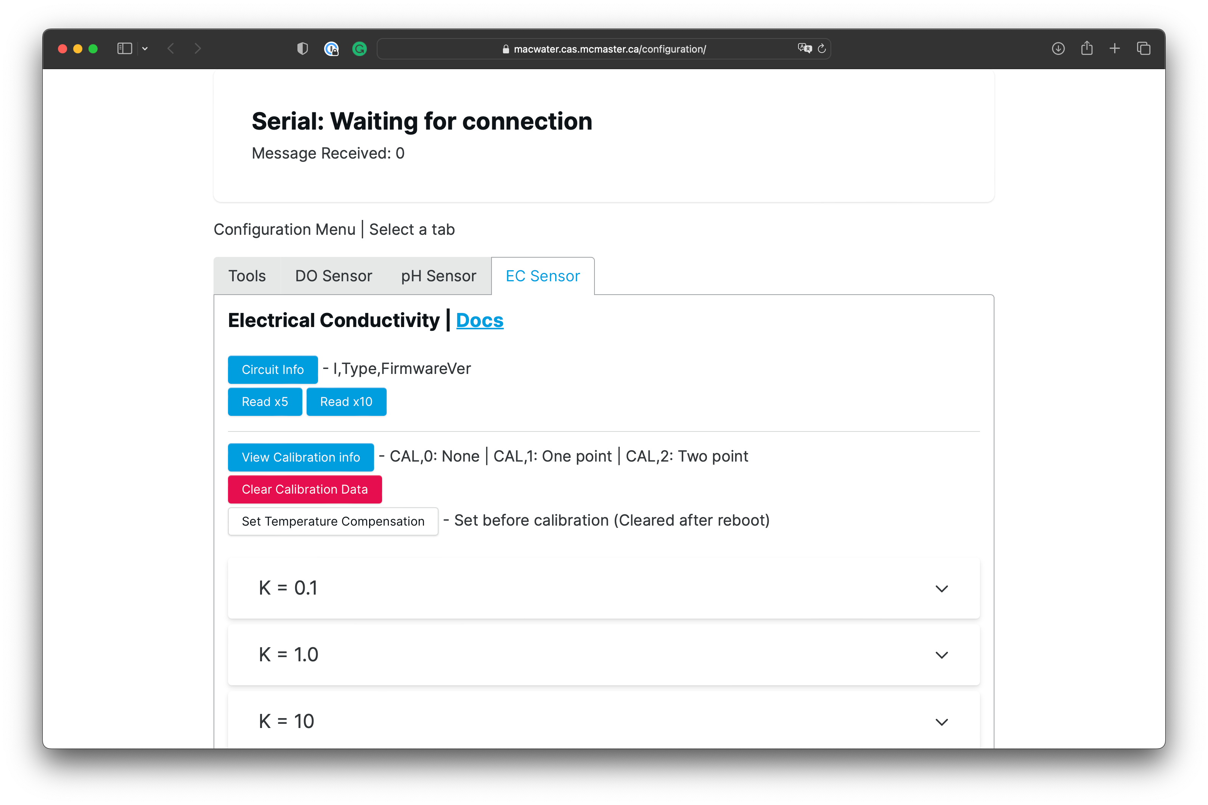
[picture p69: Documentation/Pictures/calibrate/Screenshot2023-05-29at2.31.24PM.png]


Ensure that the sensor is dry, using the `read x10` button to check when the reading is stable.

After the reading is stable, press `Calibration Air`.

### K = 0.1

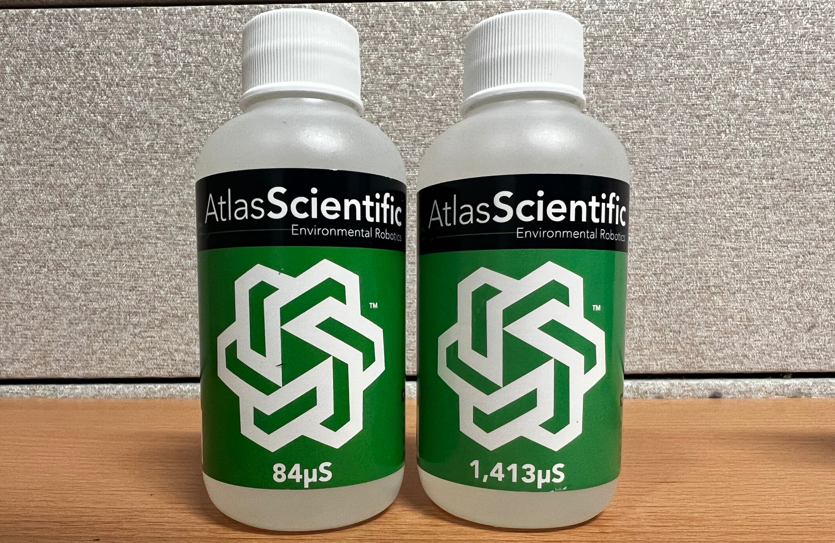
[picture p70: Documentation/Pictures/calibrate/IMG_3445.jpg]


Put the EC sensor into the 84us calibration liquid, using the `read x10` button to check that the reading is stable.

After the reading is stable, press `Calibration Low Point`.

Put the EC sensor into the 1413us calibration liquid, using the `read x10` button to check that the reading is stable.

After the reading is stable, press `Calibration High Point`.

### K = 1

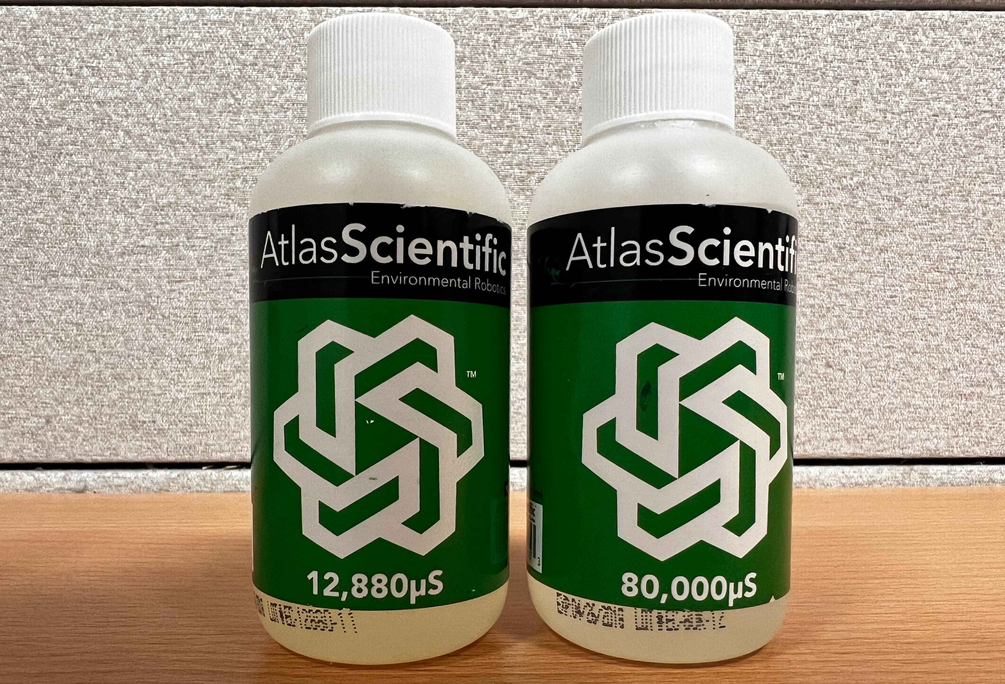
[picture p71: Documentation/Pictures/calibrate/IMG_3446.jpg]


Place the EC sensor into the 12,880us calibration liquid, using the `read x10` button to check when the reading is stable.

After the reading is stable, press `Calibration Low Point`.

Put the EC sensor into the calibration liquid 80,000us, using the `read x10` button to check when the reading is stable.

After the reading is stable, press `Calibration High Point`.

Press the `View Calibration Info` button, and make sure that the reading is `cal, 2`.

## DO Sensor Calibration

Follow the instructions in the Atlas Scientific documents to [recondition the lab-grade dissolved oxygen probe](https://files.atlas-scientific.com/LG_DO_probe.pdf#page=9)

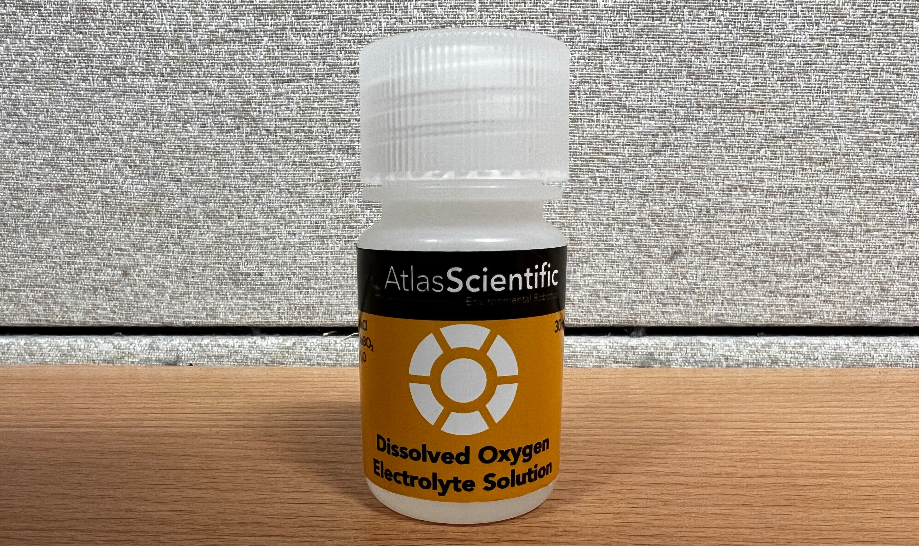
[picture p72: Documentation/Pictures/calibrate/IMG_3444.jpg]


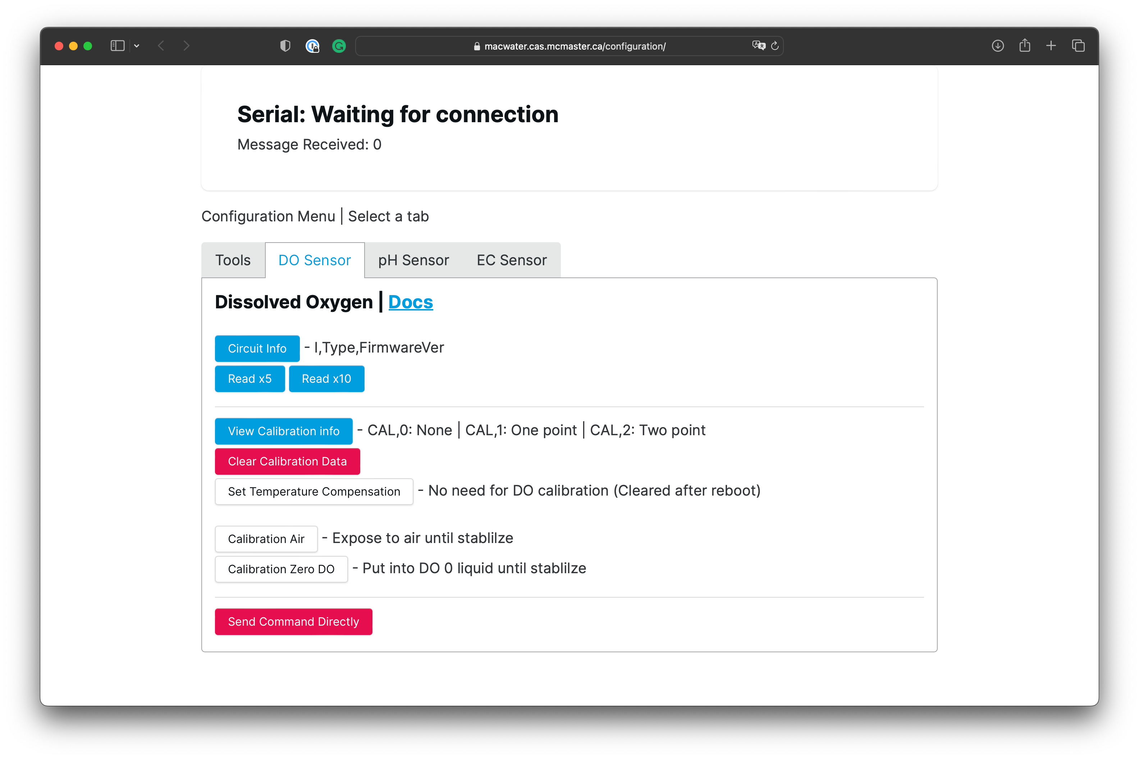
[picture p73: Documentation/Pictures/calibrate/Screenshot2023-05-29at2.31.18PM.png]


Ensure that the sensor is dry, using the `read x10` button to check when the reading is stable.

After the reading is stable, press `Calibration Air`.

Press the `View Calibration Info` button, and make sure the reading is `cal, 1`

### Calibrate with liquid only required for reading near 0.

Put the DO sensor in calibration liquid, using the `read x10` button to check when the reading is stable.

After the reading is stable, press `Calibration Zero DO`.

Press the `View Calibration Info` button, make sure that the reading is `cal, 2`

# Sensors Calibration through UART

Follow the instructions on the Atlas Scientific documents to calibrate the sensors, calibrate info is stored on the chip.

- pH
	- https://www.atlas-scientific.com/files/pH_EZO_Datasheet.pdf#page=11
- EC
	- https://www.atlas-scientific.com/files/EC_EZO_Datasheet.pdf#page=12
- DO
	- https://www.atlas-scientific.com/files/DO_EZO_Datasheet.pdf#page=9

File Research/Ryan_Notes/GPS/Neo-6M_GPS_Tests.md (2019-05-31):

# Power Management
## Settings consistent across all tests

| Setting               |   Set As   | Description/Note              |
|:---------------------:|:----------:|---                            |
|    Input Voltage      | 3V3        | The Breakout Board that the GPS chip is attached to contains a MIC5205 ultra-low dropout 3V3 regulator                            |

## Testing Procedure Outline

* Record Current Consumption during various modes that the GPS can be in:
    * Inactive for update and Inactive for search states, Acquisition state, Tracking state and Power Optimized Tracking (POT) state
* Test consumption with and without the antenna (or look up antenna power draw via datasheet)

* There is an option called _reduce peak current_. Through practice, this feature does not seem to do much. There may be a slight decrease in current drawn during the -Acquisition_ phase (1 -2mA). This decrease in power will just lead to a longer TTFF; most likly not worth enabling this feature.

## Power Save Mode
* The receiver is not able to download satellite data (e.g. the ephemeris) while it is working in ON/OFF or cyclic tracking operation.
* **When enabling Power Save Mode, SBAS support can be disabled (UBX-CFG-SBAS) since the receiver will be unable to download any SBAS data in this mode.**

* The duration for each state can be configured

### Cyclic Tracking

* Try with peak current setting on & off (no noticable change)

Aquisition Timout (minAqcTime) - 30 s  
Search Period - 20 s  
onTime (on Time) - 0 s  
update Period - 5 s  
doNotEnterOff - May enable if cannot get fix

**General State Cycle:**  
Aquisition (minAqcTime) -> Inactive for Search (Search Period) -> Aquisition (Gets fix) -> Tracking (onTime) -> POT (update Period) -> Aquisition...  

| Mode                | Average Value (mA) |
|:-------------------:|:------------------:|
| Inactive for search | 10.58              |
| Acquisition         | 51 - 53            |
| Tracking            | 38 - 40            |
|  POT                | 16 - 18            |

* Acquisition holds steady at the above ranges until a fix is obtained. After that, it flucuates between 40 - 53mA
    * I beleive at this point, it is bceause it is downloading satellities data
* After a good fix is obtained, Acquisition holds at 40 -41
    * At this point, I believe the only work being done is updating the posiion fix

### ON/OFF Operation

Aquisition Timout (minAqcTime) - 30 s  
Search Period - 20 s  
onTime (on Time) - 20 s  
update Period - 20 s  
doNotEnterOff - May enable if cannot get fix  

**General State Cycle:**  
Aquisition (minAqcTime) -> Inactive for Search (Search Period) -> Aquisition (Gets fix) -> Tracking (onTime) -> POT and Inactive for update state (Update Period) -> Aquisition...

| Mode                | Average Value (mA) |
|:-------------------:|:------------------:|
| Inactive for search | 10.58              |
| Acquisition         | 51 - 53            |
| Tracking            | 38 - 40            |
| Inactive for update | 10.57              |

* Acquisition holds steady at the above ranges until a fix is obtained. After that, it flucuates between 40 - 53mA

## Concluding Notes:

* Power SAving Mode doesn't seem to be appropriate for the Turtle Trackers. This mode is geard towards GPS's that will always remaine powered on and require position fixes relativley frequently.  
For our application the idea is to get a fix as quickly as possible, record the position, than cut all power to the GPS. The usefulness of PSM occurs after the GPS has aquired it's fix, and it is at this point that all power is cut to the GPS anyway's.   Therefore, it makes no difference to have the GPS run in Continuous mode or Power Saving Mode.

# GPS Accuracy
## Changeable Parameters

* **Use the Deviation Map, input the exact coordiantes (User-defined) than see how the acquired coordinates compare (over time)**

* **Many of these Assisting features are extremely challenging to test. It's very difficult to determine not only if the aids are being used, but if they've made any noticable difference. Their effectiveness also fluctuates with the position of the satellites**

| Setting               |   Set As   | Description                   |
|:---------------------:|:----------:|---                            |
|    Platform setting   | Pedestrian | Improve the receiver's interpretation of the measurements  and thus provide a more accurate position output. Setting  the receiver to an unsuitable platform model for the given  application environment results in a loss of receiver  performance and position accuracy.                                                            |
|      Static Mode      |   Enabled  | Allows the navigation algorithms to decrease the noise in  the position output when the velocity is below a pre-defined  ‘Static Hold Threshold’. This reduces the position wander  caused by environmental factors such as multi-path and  improves position accuracy especially in stationary applications.                      |
| NMEA Filtration Flags |     NA     | Will leave Default Settings   |
| GNSS Configuration    | Default Values | Specifies how many channels to be allocated for each satellite system (GPS, SBAS, QZSS, GLONASS). Channels are used to search for satellites. Changing the number of channels available will influence TTFF and power consumption. |
| DGNSS|     Enabled    |  See "GPS Notes"  |                            
| SBAS |     Enabled    | See "GPS Notes"   |
| Assited Data Online/Offline |    TBD   |
| Assisted Data Autonomous |     TBD   |

GNSS - Enabled  
SBAS - Enables  
Assist Autonomous - Enabled  
Jamming Monitor - Disabled (since it needs to reference a good signal first)  
Jamming Indiactor - Use it  
Update RTC & Ephemeris - Enabled?  

Messages Enabled:
    * AIDS (GPS Aiding) -> INI (Initial )

## Additional Pre-Test Notes
* Can use the Hot, Warm, and Cold commands so "one can force the receiver to reset and clear data, in order to see the effects of maintaining/losing such data between restarts."

* Manual entry of Exact GPS coordinates will be logged (found using Google Maps)

* The following data will be logged to determine effectiveness of setup and accuracy of GPS. Each will be logged for a Cold, Warm, and Hot Start. After TTFF, 100 additional indexes will be logged
    * TTFF
    * PDOP, HDOP, VDOP
    * GPS Values
        * Lat, Lon, & Alt (msl) - At TTFF
        * Lat, Lon, & Alt (msl) - Recorded 100 indexes after TTFF
        * Average Lat, Lon, & Alt (msl) - Recorded 100 Indexes after TTFF
    * Num. of satellites used

* The Data outputted by the GPS reciever can be recorded and saved.

## Test Location: Cubicle in Room 201 - ITB  
### Cold Start
### Warm Start:
### Hot Start:

## Test Location: JHE Field  

Exact GPS Coordinates: 

### Cold Start:
| Test #     | TTFF    |   PDOP    |            |
|:----------:|:--------------:| :--------:     |:-------------:     |
| 1          |                |                |                    |
| 2          |                |                |                    |
| 3          |                |                |                    |

### Warm Start:

### Hot Start:

## Test Location: Cootes Paradise  
Exact GPS Coordinates: 

### Cold Start:
### Warm Start:
### Hot Start:

## SBAS & Differential GNSS

* Enable SBAS
* View output to see if connection is established and whether GPS has improved once a connection is established
* See SBAS Section in Specs. for more info

## AssistNow Offline
* u-blox provides AlmanacPlus data files in different sizes, which contain differential almanac corrections that are valid for a period of between 1 and 14 days thereafter.
* Requires an external memory device connected to the GPS chip using SPI. Alternativly, the data can be saved on thr Arduino (or maybe computer for testing) as the 'Host' and sent via the EX/TX pins to the GPS chip

## AssistNow Autonomous
* Prevents Power Save Mode from being entered until calculations are done
* AssistNow Autonomous subsystem will not produce any data and orbits while AssistNow Offline data is available

## Jamming Test
### Jamming/Interference Indicator Test
* Must be calibrated to indicate what a 'not jammed' case would be

### Jamming/Interference Monitor
* Cannot be used in Power Save Mode
* Must aquire a good fix for comparison if jamming occurs
* Must set the Thresholds for what would be classified as 'jamming'

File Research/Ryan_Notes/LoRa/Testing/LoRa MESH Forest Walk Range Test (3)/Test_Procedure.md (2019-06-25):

# Test 2: Forest Walk  Test
## Test Procedure

The Gateway will be set up at a static location, preferably at a location higher than where the nodes will be. Two nodes will be taken on a walk In the forest near the track. One will use the DIY Helical antenna, the other will use a more heavy duty antenna (one that a Gateway may use). The antennas to use will be determined from the previous test done (RSSI Test). The nodes will acquire a GPS fix and, every 15 seconds, transmit the coordinates to the Gateway. The nodes will save any coordinates that were sent unsuccessfully on the Arduino's EEPROM. Upon completion, the GPS coordinates received by the Gateway can be compared with that of the GPS coordinates stored to see at what locations the transmission failed.  
The Gateway will save the received data and RSSI values to an SD card. Someone watching over the Gateway can report if data has stopped being received.

## Node Setup
### General

* LoRa MESH Module Connected to Arduino Nano
* LoRa MESH communicates with Arduino via AltSoftSerial
* GPS communicates with Arduino via HardwareSerial
* Debugging is done via SoftwareSerial using Putty (an adapter must be used to power the Arduino rather than the USB cord provided)
* **Node 1 uses the White LoRa Antenna, while Node 2 uses the DIY Helical Wire Antenna (both shown in the RSSi Test)**

### Pinout

| LoRa   |   Arduino  |
|:------:|:----------:|
| GND    |  GND  	  |
| VCC    |   5V  	  |  
| RX     |   D9  	  |  
| TX     |   D8  	  |  

| GPS   |   Arduino  |
|:------:|:----------:|
| GND    |  GND  	  |
| VCC    |   5V  	  |  
| RX     |   TX  	  |  
| TX     |   RX  	  |  

| PC   |   Arduino  |
|:------:|:----------:|
| GND    |  GND  	  |
| VCC    |   5V  	  |  
| RX     |   D3  	  |  
| TX     |   D2  	  |  

### Hardware




## Gateway Setup
### General

* LoRa MESH Module Connected to Arduino Uno
* LoRa MESH communicates with Arduino via AltSoftSerial
* GPS communicates with Arduino via HardwareSerial
* Debugging is done via SoftwareSerial using the Arduino Serial Monitor
* Data read/write to SD card via Arduino's **dedicated SPI pins**

### Pinout

| LoRa   |   Arduino  |
|:------:|:----------:|
| GND    |  GND  	  |
| VCC    |   5V  	  |  
| RX     |   D9  	  |  
| TX     |   D8  	  |  

| PC   |   Arduino  |
|:------:|:----------:|
| GND    |  GND  	  |
| VCC    |   5V  	  |  
| RX     |   D3  	  |  
| TX     |   D2  	  | 

### Hardware



# Result & Notes
## Results
* A Preliminary Test was done at ITB to ensure the test was working properly. The results can be found in the excel file, in the heading labelled "Preliminary Test"
* Data can be viewed in the Excel file "Forest Walk Data.xlsv"
* The Gateway was moved at one point during the test. This can be seen from where the black lines starts.

That data can be view and  examined [here][Map Site]. It has been summarized below in case the link no longer works:  

Dark Purple - Data received  
Orange - Data not received  


Dark Blue - Data received  


Data was not saved to the Node's EEPROM to view the GPS coordinates that were not successfully test. As such, another test (shown below) was done using this node

Green - Data received  
Dark Blue - Data not received  


## Notes

* There appeared to be an issue with receiving data when Node 1 and Node 2 sent data at the same time
* If the Gateway is to be placed on a hill, ensure that the hill drops off immediately. Otherwise, the earth my block the transmission. This is why the Gateway was moved during the test.

[Map Site]: https://mapmakerapp.com?map=5d0d363ed4a9e062847053ff28ae
[Node 1 & Node 1 (Gateway)]: https://i.ibb.co/tDjdfm4/Node-1-Node-1-Gateway.png
[Node 2 (Gateway)]: https://i.ibb.co/ZGHZ3zh/Node-2-Node-2-Gateway.png
[Node 2 & Node 2 (Gateway)]: https://i.ibb.co/k6mWMtR/Node-2.png

[Node Setup 1]: https://i.ibb.co/x6nd0kT/Node-Setup-1.jpg
[Node Setup 2]: https://i.ibb.co/8MD8q6L/Node-Setup-2.jpg
[Gateway Setup 1]: https://i.ibb.co/MBP10c6/Gateway-Setup-2.jpg

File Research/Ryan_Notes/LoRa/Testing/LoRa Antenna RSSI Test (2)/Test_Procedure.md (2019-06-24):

# Test Outline

1. Construct a Helical Antenna using a guide below
    * Will need to remove SMA connector of MESH modules to connect the antenna
2. Configure MESH Module to match antenna attached to it
	* Big one here is frequency
2. Test to determine which antenna to use for Trackers.
    * Gateway antenna does not matter too much. Use one with good receiver sensitivity
    * Do RSSI test to see how Tracker antenna performs
        * Set Modules and antenna up at set distance. Send data, compare RSSi values. Do this for different orientations and distances 
            * Must be specific with set-up. Distance, elevation, weather conditions, etc.
        * NOTE: to try DIY Helic Antenna, SMA connector of MESH module must be removed 
2. Determine which antenna will be used
    * NOTE: Gateways are not limited to the weight or space constraint the Trackers are, so a different antenna may be used. The antenna used by the Gateway cannot improve the distance the turtles can travel, but it can improve the separation distance between other Gateways. Only requirement is good receiver sensitivity

# Testing Info
## Testing Environment
 [[6]]

* For tests that yield usable data, you should be testing your network at several locations. In addition, the the following metadata should be recorded, [[6]]
	* You should be testing your network at several locations
	* Location (lat, lon)
	* Height (above/below ground)
	* Surrounding (building inside/outside, forest, street etc.)
	* Weather conditions

## Test Values
**RSSI**: indication of the radio power level being received by the device [[6]]

*  In general you can say, the higher the RSSI number, the stronger the signal
	* But the number does not linearly correspond to the distance between transmitter and receiver. 
	* RSSI won’t tell you much about the bigger picture, especially if you only measure some spots and for a short period of time. 
	* In addition the signal strength (in dBm) is subject to a logarithmic loss dependent on the distance.
* The lower you get (less than -100), the less linear correlation you will have between the distance (in free space) and the RSSI value. The lower the value, the less valuable information you get out of the RSSI value alone.
 
## Test Procedures Available

[DIY Test using RSSI values][DIY RSSI Test]  
* A simple test to compare the performance of different antennas using the RSSI value

[DIY LoRa Range Test][DIY LoRa Range Test]
* Travel the area with a LoRa device that transmits GPS coordiantes. In addition, track where you've travelled using GPS. Compare what GPS data was recieved with the GPS data that tracked where you've travelled to see what was recieved and what was not

# Test 1: RSSI Test
## Test Outline

Two nodes will be placed 50m apart, at waist height. One node (host) will transmit dummy data to the other node (client). The client node will then send back the recorded RSSi value associated with that dummy load. The host node will receive this data (the first RSSI value), along with the associated RSSI value. This will de done 10 times, the two RSSI values will be averaged and displayed. This will be done with various antennas to get a general idea of their performance.

An additional test will be done where the node is enclosed in a casing similar to what will be used to protect/waterproof the tracker. THis will enable us to see how much the enclosure limits the range of Trackers LoRa.

The Client will be the Node with the same Antenna for all Tests

## Host Setup
### General

* LoRa MESH Module Connected to Arduino Nano
* Arduino Code -> found in 'Ryan Tyrrell19/Code/Antenna_RSSI_Test/LoRa_RSSI_Test_Host.ino'
* LoRa MESH communicates with Arduino via SoftwareSerial

### Pinout

LoRa   |   Arduino  
GND    ->   GND  
VCC    ->   5V  
RX     ->   D2  
TX     ->   D3  

## CLient Setup
### General
* LoRa MESH Module Connected to Arduino Uno
* Arduino Code -> found in 'Ryan Tyrrell19/Code/Antenna_RSSI_Test/LoRa_RSSI_Test_Client.ino'
* LoRa MESH communicates with Arduino via SoftwareSerial

### Pinout
LoRa   |   Arduino  
GND    ->   GND  
VCC    ->   5V  
RX     ->   D2  
TX     ->   D3  

## Test Procedure & Results

The following antenna will be used for the Client:



The following antennas will be tested with the Host:



The antennas will be tested from left to right, with the last one representing no antenna.

The following location is where the test will be conducted:



[6]: https://lorawantester.com/2019/01/09/5-simple-rules-to-guarantee-a-successful-lorawan-coverage-test/

[DIY RSSI Test]: http://www.ph2lb.nl/blog/index.php?page=lora-measuring-antennas
[DIY LoRa Range Test]: https://reibot.org/2017/04/23/lora-range-test/

[Antenna Test 1]: https://www.coredump.ch/2017/04/30/lorawan-868mhz-antenna-test-part-2/
[Antenna Test 2]: https://medium.com/home-wireless/testing-lora-antennas-at-915mhz-6d6b41ac8f1d
[Testing Environment]: https://i.ibb.co/VVbH171/6.png

[Gateway Antenna]: https://i.ibb.co/x2M60vc/Gateway-Antennas.jpg
[Test Antennas]: https://i.ibb.co/VBMqhqq/Test-Antennas.jpg

[RSSI Test Area]: https://i.ibb.co/bQqkWgL/7.png

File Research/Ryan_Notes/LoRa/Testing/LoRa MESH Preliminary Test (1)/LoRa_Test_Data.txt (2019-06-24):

Configuration Setup:

 0x01 0x00 0x02 0x00 0x03

FrameType = 0x01
CmdType = 0x82
flag = 0xA5A5
channel = 0x01
txPower = 0x00
uiMode = 0x00
eqType = 0x01
netId = 0x0000
nodeId = 0x1234
serPortParam = 0x40
airRate = 0x0909

-------------------
Waiting for Data...
srcAddr =  0x0001
power =  0x2F
userPayloadLength =  0x04
Payload:
 0xFF 0xEE 0xDD 0xCC
-------------------
-------------------
Waiting for Data...
srcAddr =  0x0001
power =  0x2E
userPayloadLength =  0x04
Payload:
 0xFF 0xEE 0xDD 0xCC
-------------------
-------------------
Waiting for Data...
srcAddr =  0x0001
power =  0x2E
userPayloadLength =  0x04
Payload:
 0xFF 0xEE 0xDD 0xCC
-------------------
-------------------
Waiting for Data...
srcAddr =  0x0001
power =  0x2E
userPayloadLength =  0x04
Payload:
 0xFF 0xEE 0xDD 0xCC
-------------------
-------------------
Waiting for Data...
srcAddr =  0x0001
power =  0x34
userPayloadLength =  0x04
Payload:
 0xFF 0xEE 0xDD 0xCC
-------------------
-------------------
Waiting for Data...
srcAddr =  0x0001
power =  0x2F
userPayloadLength =  0x04
Payload:
 0xFF 0xEE 0xDD 0xCC
-------------------
-------------------
Waiting for Data...
srcAddr =  0x0001
power =  0x35
userPayloadLength =  0x04
Payload:
 0xFF 0xEE 0xDD 0xCC
-------------------
-------------------
Waiting for Data...
srcAddr =  0x0001
power =  0x35
userPayloadLength =  0x04
Payload:
 0xFF 0xEE 0xDD 0xCC
-------------------
-------------------
Waiting for Data...
srcAddr =  0x0001
power =  0x33
userPayloadLength =  0x04
Payload:
 0xFF 0xEE 0xDD 0xCC
-------------------
-------------------
Waiting for Data...
srcAddr =  0x0001
power =  0x3D
userPayloadLength =  0x04
Payload:
 0xFF 0xEE 0xDD 0xCC
-------------------
-------------------
Waiting for Data...
srcAddr =  0x0001
power =  0x37
userPayloadLength =  0x04
Payload:
 0xFF 0xEE 0xDD 0xCC
-------------------
-------------------
Waiting for Data...
srcAddr =  0x0001
power =  0x36
userPayloadLength =  0x04
Payload:
 0xFF 0xEE 0xDD 0xCC
-------------------
-------------------
Waiting for Data...
srcAddr =  0x0001
power =  0x2B
userPayloadLength =  0x04
Payload:
 0xFF 0xEE 0xDD 0xCC
-------------------
-------------------
Waiting for Data...
srcAddr =  0x0001
power =  0x29
userPayloadLength =  0x04
Payload:
 0xFF 0xEE 0xDD 0xCC
-------------------
-------------------
Waiting for Data...
srcAddr =  0x0001
power =  0x2A
userPayloadLength =  0x04
Payload:
 0xFF 0xEE 0xDD 0xCC
-------------------
-------------------
Waiting for Data...
srcAddr =  0x0001
power =  0x30
userPayloadLength =  0x04
Payload:
 0xFF 0xEE 0xDD 0xCC
-------------------
-------------------
Waiting for Data...
srcAddr =  0x0001
power =  0x2E
userPayloadLength =  0x04
Payload:
 0xFF 0xEE 0xDD 0xCC
-------------------
-------------------
Waiting for Data...
srcAddr =  0x0001
power =  0x2E
userPayloadLength =  0x04
Payload:
 0xFF 0xEE 0xDD 0xCC
-------------------
-------------------
Waiting for Data...
srcAddr =  0x0001
power =  0x2C
userPayloadLength =  0x04
Payload:
 0xFF 0xEE 0xDD 0xCC
-------------------
-------------------
Waiting for Data...
srcAddr =  0x0001
power =  0x2D
userPayloadLength =  0x04
Payload:
 0xFF 0xEE 0xDD 0xCC
-------------------
-------------------
Waiting for Data...
srcAddr =  0x0001
power =  0x2B
userPayloadLength =  0x04
Payload:
 0xFF 0xEE 0xDD 0xCC
-------------------
-------------------
Waiting for Data...
srcAddr =  0x0001
power =  0x2F
userPayloadLength =  0x04
Payload:
 0xFF 0xEE 0xDD 0xCC
-------------------
-------------------
Waiting for Data...
srcAddr =  0x0001
power =  0x2F
userPayloadLength =  0x04
Payload:
 0xFF 0xEE 0xDD 0xCC
-------------------
-------------------
Waiting for Data...
srcAddr =  0x0001
power =  0x2A
userPayloadLength =  0x04
Payload:
 0xFF 0xEE 0xDD 0xCC
-------------------
-------------------
Waiting for Data...
srcAddr =  0x0001
power =  0x31
userPayloadLength =  0x04
Payload:
 0xFF 0xEE 0xDD 0xCC
-------------------
-------------------
Waiting for Data...
srcAddr =  0x0001
power =  0x36
userPayloadLength =  0x04
Payload:
 0xFF 0xEE 0xDD 0xCC
-------------------
-------------------
Waiting for Data...
srcAddr =  0x0001
power =  0x36
userPayloadLength =  0x04
Payload:
 0xFF 0xEE 0xDD 0xCC
-------------------
-------------------
Waiting for Data...
srcAddr =  0x0001
power =  0x35
userPayloadLength =  0x04
Payload:
 0xFF 0xEE 0xDD 0xCC
-------------------
-------------------
Waiting for Data...
srcAddr =  0x0001
power =  0x37
userPayloadLength =  0x04
Payload:
 0xFF 0xEE 0xDD 0xCC
-------------------
-------------------
Waiting for Data...
srcAddr =  0x0001
power =  0x40
userPayloadLength =  0x04
Payload:
 0xFF 0xEE 0xDD 0xCC
-------------------
-------------------
Waiting for Data...
srcAddr =  0x0001
power =  0x3B
userPayloadLength =  0x04
Payload:
 0xFF 0xEE 0xDD 0xCC
-------------------
-------------------
Waiting for Data...
srcAddr =  0x0001
power =  0x3E
userPayloadLength =  0x04
Payload:
 0xFF 0xEE 0xDD 0xCC
-------------------
-------------------
Waiting for Data...
srcAddr =  0x0001
power =  0x30
userPayloadLength =  0x04
Payload:
 0xFF 0xEE 0xDD 0xCC
-------------------
-------------------
Waiting for Data...
srcAddr =  0x0001
power =  0x3A
userPayloadLength =  0x04
Payload:
 0xFF 0xEE 0xDD 0xCC
-------------------
-------------------
Waiting for Data...
srcAddr =  0x0001
power =  0x41
userPayloadLength =  0x04
Payload:
 0xFF 0xEE 0xDD 0xCC
-------------------
-------------------
Waiting for Data...
srcAddr =  0x0001
power =  0x3D
userPayloadLength =  0x04
Payload:
 0xFF 0xEE 0xDD 0xCC
-------------------
-------------------
Waiting for Data...
srcAddr =  0x0001
power =  0x3E
userPayloadLength =  0x04
Payload:
 0xFF 0xEE 0xDD 0xCC
-------------------
-------------------
Waiting for Data...
srcAddr =  0x0001
power =  0x3D
userPayloadLength =  0x04
Payload:
 0xFF 0xEE 0xDD 0xCC
-------------------
-------------------
Waiting for Data...
srcAddr =  0x0001
power =  0x3F
userPayloadLength =  0x04
Payload:
 0xFF 0xEE 0xDD 0xCC
-------------------
-------------------
Waiting for Data...
srcAddr =  0x0001
power =  0x41
userPayloadLength =  0x04
Payload:
 0xFF 0xEE 0xDD 0xCC
-------------------
-------------------
Waiting for Data...
srcAddr =  0x0001
power =  0x41
userPayloadLength =  0x04
Payload:
 0xFF 0xEE 0xDD 0xCC
-------------------
-------------------
Waiting for Data...
srcAddr =  0x0001
power =  0x45
userPayloadLength =  0x04
Payload:
 0xFF 0xEE 0xDD 0xCC
-------------------
-------------------
Waiting for Data...
srcAddr =  0x0001
power =  0x41
userPayloadLength =  0x04
Payload:
 0xFF 0xEE 0xDD 0xCC
-------------------
-------------------
Waiting for Data...
srcAddr =  0x0001
power =  0x3B
userPayloadLength =  0x04
Payload:
 0xFF 0xEE 0xDD 0xCC
-------------------
-------------------
Waiting for Data...
srcAddr =  0x0001
power =  0x38
userPayloadLength =  0x04
Payload:
 0xFF 0xEE 0xDD 0xCC
-------------------
-------------------
Waiting for Data...
srcAddr =  0x0001
power =  0x48
userPayloadLength =  0x04
Payload:
 0xFF 0xEE 0xDD 0xCC
-------------------
-------------------
Waiting for Data...
srcAddr =  0x0001
power =  0x4D
userPayloadLength =  0x04
Payload:
 0xFF 0xEE 0xDD 0xCC
-------------------
-------------------
Waiting for Data...
srcAddr =  0x0001
power =  0x4A
userPayloadLength =  0x04
Payload:
 0xFF 0xEE 0xDD 0xCC
-------------------
-------------------
Waiting for Data...
srcAddr =  0x0001
power =  0x45
userPayloadLength =  0x04
Payload:
 0xFF 0xEE 0xDD 0xCC
-------------------
-------------------
Waiting for Data...
srcAddr =  0x0001
power =  0x45
userPayloadLength =  0x04
Payload:
 0xFF 0xEE 0xDD 0xCC
-------------------
-------------------
Waiting for Data...
srcAddr =  0x0001
power =  0x4C
userPayloadLength =  0x04
Payload:
 0xFF 0xEE 0xDD 0xCC
-------------------
-------------------
Waiting for Data...
srcAddr =  0x0001
power =  0x42
userPayloadLength =  0x04
Payload:
 0xFF 0xEE 0xDD 0xCC
-------------------
-------------------
Waiting for Data...
srcAddr =  0x0001
power =  0x43
userPayloadLength =  0x04
Payload:
 0xFF 0xEE 0xDD 0xCC
-------------------
-------------------
Waiting for Data...
srcAddr =  0x0001
power =  0x43
userPayloadLength =  0x04
Payload:
 0xFF 0xEE 0xDD 0xCC
-------------------
-------------------
Waiting for Data...
srcAddr =  0x0001
power =  0x59
userPayloadLength =  0x04
Payload:
 0xFF 0xEE 0xDD 0xCC
-------------------
-------------------
Waiting for Data...
srcAddr =  0x0001
power =  0x4C
userPayloadLength =  0x04
Payload:
 0xFF 0xEE 0xDD 0xCC
-------------------
-------------------
Waiting for Data...
srcAddr =  0x0001
power =  0x5F
userPayloadLength =  0x04
Payload:
 0xFF 0xEE 0xDD 0xCC
-------------------
-------------------
Waiting for Data...
srcAddr =  0x0001
power =  0x59
userPayloadLength =  0x04
Payload:
 0xFF 0xEE 0xDD 0xCC
-------------------
-------------------
Waiting for Data...
srcAddr =  0x0001
power =  0x56
userPayloadLength =  0x04
Payload:
 0xFF 0xEE 0xDD 0xCC
-------------------
-------------------
Waiting for Data...
srcAddr =  0x0001
power =  0x5C
userPayloadLength =  0x04
Payload:
 0xFF 0xEE 0xDD 0xCC
-------------------
-------------------
Waiting for Data...
srcAddr =  0x0001
power =  0x60
userPayloadLength =  0x04
Payload:
 0xFF 0xEE 0xDD 0xCC
-------------------
-------------------
Waiting for Data...
srcAddr =  0x0001
power =  0x61
userPayloadLength =  0x04
Payload:
 0xFF 0xEE 0xDD 0xCC
-------------------
-------------------
Waiting for Data...
srcAddr =  0x0001
power =  0x60
userPayloadLength =  0x04
Payload:
 0xFF 0xEE 0xDD 0xCC
-------------------
-------------------
Waiting for Data...
srcAddr =  0x0001
power =  0x58
userPayloadLength =  0x04
Payload:
 0xFF 0xEE 0xDD 0xCC
-------------------
-------------------
Waiting for Data...
srcAddr =  0x0001
power =  0x57
userPayloadLength =  0x04
Payload:
 0xFF 0xEE 0xDD 0xCC
-------------------
-------------------
Waiting for Data...
srcAddr =  0x0001
power =  0x5C
userPayloadLength =  0x04
Payload:
 0xFF 0xEE 0xDD 0xCC
-------------------
-------------------
Waiting for Data...
srcAddr =  0x0001
power =  0x5A
userPayloadLength =  0x04
Payload:
 0xFF 0xEE 0xDD 0xCC
-------------------
-------------------
Waiting for Data...
srcAddr =  0x0001
power =  0x5F
userPayloadLength =  0x04
Payload:
 0xFF 0xEE 0xDD 0xCC
-------------------
-------------------
Waiting for Data...
srcAddr =  0x0001
power =  0x58
userPayloadLength =  0x04
Payload:
 0xFF 0xEE 0xDD 0xCC
-------------------
-------------------
Waiting for Data...
srcAddr =  0x0001
power =  0x5F
userPayloadLength =  0x04
Payload:
 0xFF 0xEE 0xDD 0xCC
-------------------
-------------------
Waiting for Data...
srcAddr =  0x0001
power =  0x57
userPayloadLength =  0x04
Payload:
 0xFF 0xEE 0xDD 0xCC
-------------------
-------------------
Waiting for Data...
srcAddr =  0x0001
power =  0x5E
userPayloadLength =  0x04
Payload:
 0xFF 0xEE 0xDD 0xCC
-------------------
-------------------
Waiting for Data...
srcAddr =  0x0001
power =  0x5E
userPayloadLength =  0x04
Payload:
 0xFF 0xEE 0xDD 0xCC
-------------------
-------------------
Waiting for Data...
srcAddr =  0x0001
power =  0x5C
userPayloadLength =  0x04
Payload:
 0xFF 0xEE 0xDD 0xCC
-------------------
-------------------
Waiting for Data...
srcAddr =  0x0001
power =  0x5A
userPayloadLength =  0x04
Payload:
 0xFF 0xEE 0xDD 0xCC
-------------------
-------------------
Waiting for Data...
srcAddr =  0x0001
power =  0x5A
userPayloadLength =  0x04
Payload:
 0xFF 0xEE 0xDD 0xCC
-------------------
-------------------
Waiting for Data...
srcAddr =  0x0001
power =  0x56
userPayloadLength =  0x04
Payload:
 0xFF 0xEE 0xDD 0xCC
-------------------
-------------------
Waiting for Data...
srcAddr =  0x0001
power =  0x52
userPayloadLength =  0x04
Payload:
 0xFF 0xEE 0xDD 0xCC
-------------------
-------------------
Waiting for Data...
srcAddr =  0x0001
power =  0x56
userPayloadLength =  0x04
Payload:
 0xFF 0xEE 0xDD 0xCC
-------------------
-------------------
Waiting for Data...
srcAddr =  0x0001
power =  0x5C
userPayloadLength =  0x04
Payload:
 0xFF 0xEE 0xDD 0xCC
-------------------
-------------------
Waiting for Data...
srcAddr =  0x0001
power =  0x53
userPayloadLength =  0x04
Payload:
 0xFF 0xEE 0xDD 0xCC
-------------------
-------------------
Waiting for Data...
srcAddr =  0x0001
power =  0x58
userPayloadLength =  0x04
Payload:
 0xFF 0xEE 0xDD 0xCC
-------------------
-------------------
Waiting for Data...
srcAddr =  0x0001
power =  0x5A
userPayloadLength =  0x04
Payload:
 0xFF 0xEE 0xDD 0xCC
-------------------
-------------------
Waiting for Data...
srcAddr =  0x0001
power =  0x53
userPayloadLength =  0x04
Payload:
 0xFF 0xEE 0xDD 0xCC
-------------------
-------------------
Waiting for Data...
srcAddr =  0x0001
power =  0x4F
userPayloadLength =  0x04
Payload:
 0xFF 0xEE 0xDD 0xCC
-------------------
-------------------
Waiting for Data...
srcAddr =  0x0001
power =  0x5A
userPayloadLength =  0x04
Payload:
 0xFF 0xEE 0xDD 0xCC
-------------------
-------------------
Waiting for Data...
srcAddr =  0x0001
power =  0x62
userPayloadLength =  0x04
Payload:
 0xFF 0xEE 0xDD 0xCC
-------------------
-------------------
Waiting for Data...
srcAddr =  0x0001
power =  0x54
userPayloadLength =  0x04
Payload:
 0xFF 0xEE 0xDD 0xCC
-------------------
-------------------
Waiting for Data...
srcAddr =  0x0001
power =  0x63
userPayloadLength =  0x04
Payload:
 0xFF 0xEE 0xDD 0xCC
-------------------
-------------------
Waiting for Data...
srcAddr =  0x0001
power =  0x66
userPayloadLength =  0x04
Payload:
 0xFF 0xEE 0xDD 0xCC
-------------------
-------------------
Waiting for Data...
srcAddr =  0x0001
power =  0x59
userPayloadLength =  0x04
Payload:
 0xFF 0xEE 0xDD 0xCC
-------------------
-------------------
Waiting for Data...
srcAddr =  0x0001
power =  0x55
userPayloadLength =  0x04
Payload:
 0xFF 0xEE 0xDD 0xCC
-------------------
-------------------
Waiting for Data...
srcAddr =  0x0001
power =  0x58
userPayloadLength =  0x04
Payload:
 0xFF 0xEE 0xDD 0xCC
-------------------
-------------------
Waiting for Data...
srcAddr =  0x0001
power =  0x5C
userPayloadLength =  0x04
Payload:
 0xFF 0xEE 0xDD 0xCC
-------------------
-------------------
Waiting for Data...
srcAddr =  0x0001
power =  0x54
userPayloadLength =  0x04
Payload:
 0xFF 0xEE 0xDD 0xCC
-------------------
-------------------
Waiting for Data...
srcAddr =  0x0001
power =  0x5D
userPayloadLength =  0x04
Payload:
 0xFF 0xEE 0xDD 0xCC
-------------------
-------------------
Waiting for Data...
srcAddr =  0x0001
power =  0x51
userPayloadLength =  0x04
Payload:
 0xFF 0xEE 0xDD 0xCC
-------------------
-------------------
Waiting for Data...
srcAddr =  0x0001
power =  0x58
userPayloadLength =  0x04
Payload:
 0xFF 0xEE 0xDD 0xCC
-------------------
-------------------
Waiting for Data...
srcAddr =  0x0001
power =  0x50
userPayloadLength =  0x04
Payload:
 0xFF 0xEE 0xDD 0xCC
-------------------
-------------------
Waiting for Data...
srcAddr =  0x0001
power =  0x54
userPayloadLength =  0x04
Payload:
 0xFF 0xEE 0xDD 0xCC
-------------------
-------------------
Waiting for Data...
srcAddr =  0x0001
power =  0x4E
userPayloadLength =  0x04
Payload:
 0xFF 0xEE 0xDD 0xCC
-------------------
-------------------
Waiting for Data...
srcAddr =  0x0001
power =  0x52
userPayloadLength =  0x04
Payload:
 0xFF 0xEE 0xDD 0xCC
-------------------
-------------------
Waiting for Data...
srcAddr =  0x0001
power =  0x57
userPayloadLength =  0x04
Payload:
 0xFF 0xEE 0xDD 0xCC
-------------------
-------------------
Waiting for Data...
srcAddr =  0x0001
power =  0x5E
userPayloadLength =  0x04
Payload:
 0xFF 0xEE 0xDD 0xCC
-------------------
-------------------
Waiting for Data...
srcAddr =  0x0001
power =  0x78
userPayloadLength =  0x04
Payload:
 0xFF 0xEE 0xDD 0xCC
-------------------
-------------------
Waiting for Data...
srcAddr =  0x0001
power =  0x62
userPayloadLength =  0x04
Payload:
 0xFF 0xEE 0xDD 0xCC
-------------------
-------------------
Waiting for Data...
srcAddr =  0x0001
power =  0x62
userPayloadLength =  0x04
Payload:
 0xFF 0xEE 0xDD 0xCC
-------------------
-------------------
Waiting for Data...
srcAddr =  0x0001
power =  0x66
userPayloadLength =  0x04
Payload:
 0xFF 0xEE 0xDD 0xCC
-------------------
-------------------
Waiting for Data...
srcAddr =  0x0001
power =  0x60
userPayloadLength =  0x04
Payload:
 0xFF 0xEE 0xDD 0xCC
-------------------
-------------------
Waiting for Data...
srcAddr =  0x0001
power =  0x58
userPayloadLength =  0x04
Payload:
 0xFF 0xEE 0xDD 0xCC
-------------------
-------------------
Waiting for Data...
srcAddr =  0x0001
power =  0x73
userPayloadLength =  0x04
Payload:
 0xFF 0xEE 0xDD 0xCC
-------------------
-------------------
Waiting for Data...
srcAddr =  0x0001
power =  0x5F
userPayloadLength =  0x04
Payload:
 0xFF 0xEE 0xDD 0xCC
-------------------
-------------------
Waiting for Data...
srcAddr =  0x0001
power =  0x60
userPayloadLength =  0x04
Payload:
 0xFF 0xEE 0xDD 0xCC
-------------------
-------------------
Waiting for Data...
srcAddr =  0x0001
power =  0x6B
userPayloadLength =  0x04
Payload:
 0xFF 0xEE 0xDD 0xCC
-------------------
-------------------
Waiting for Data...
srcAddr =  0x0001
power =  0x62
userPayloadLength =  0x04
Payload:
 0xFF 0xEE 0xDD 0xCC
-------------------
-------------------
Waiting for Data...
srcAddr =  0x0001
power =  0x5A
userPayloadLength =  0x04
Payload:
 0xFF 0xEE 0xDD 0xCC
-------------------
-------------------
Waiting for Data...
srcAddr =  0x0001
power =  0x74
userPayloadLength =  0x04
Payload:
 0xFF 0xEE 0xDD 0xCC
-------------------
-------------------
Waiting for Data...
srcAddr =  0x0001
power =  0x75
userPayloadLength =  0x04
Payload:
 0xFF 0xEE 0xDD 0xCC
-------------------
-------------------
Waiting for Data...
srcAddr =  0x0001
power =  0x69
userPayloadLength =  0x04
Payload:
 0xFF 0xEE 0xDD 0xCC
-------------------
-------------------
Waiting for Data...
srcAddr =  0x0001
power =  0x69
userPayloadLength =  0x04
Payload:
 0xFF 0xEE 0xDD 0xCC
-------------------
-------------------
Waiting for Data...
srcAddr =  0x0001
power =  0x61
userPayloadLength =  0x04
Payload:
 0xFF 0xEE 0xDD 0xCC
-------------------
-------------------
Waiting for Data...
srcAddr =  0x0001
power =  0x69
userPayloadLength =  0x04
Payload:
 0xFF 0xEE 0xDD 0xCC
-------------------
-------------------
Waiting for Data...
srcAddr =  0x0001
power =  0x69
userPayloadLength =  0x04
Payload:
 0xFF 0xEE 0xDD 0xCC
-------------------
-------------------
Waiting for Data...
srcAddr =  0x0001
power =  0x67
userPayloadLength =  0x04
Payload:
 0xFF 0xEE 0xDD 0xCC
-------------------
-------------------
Waiting for Data...
srcAddr =  0x0001
power =  0x66
userPayloadLength =  0x04
Payload:
 0xFF 0xEE 0xDD 0xCC
-------------------
-------------------
Waiting for Data...
srcAddr =  0x0001
power =  0x68
userPayloadLength =  0x04
Payload:
 0xFF 0xEE 0xDD 0xCC
-------------------
-------------------
Waiting for Data...
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

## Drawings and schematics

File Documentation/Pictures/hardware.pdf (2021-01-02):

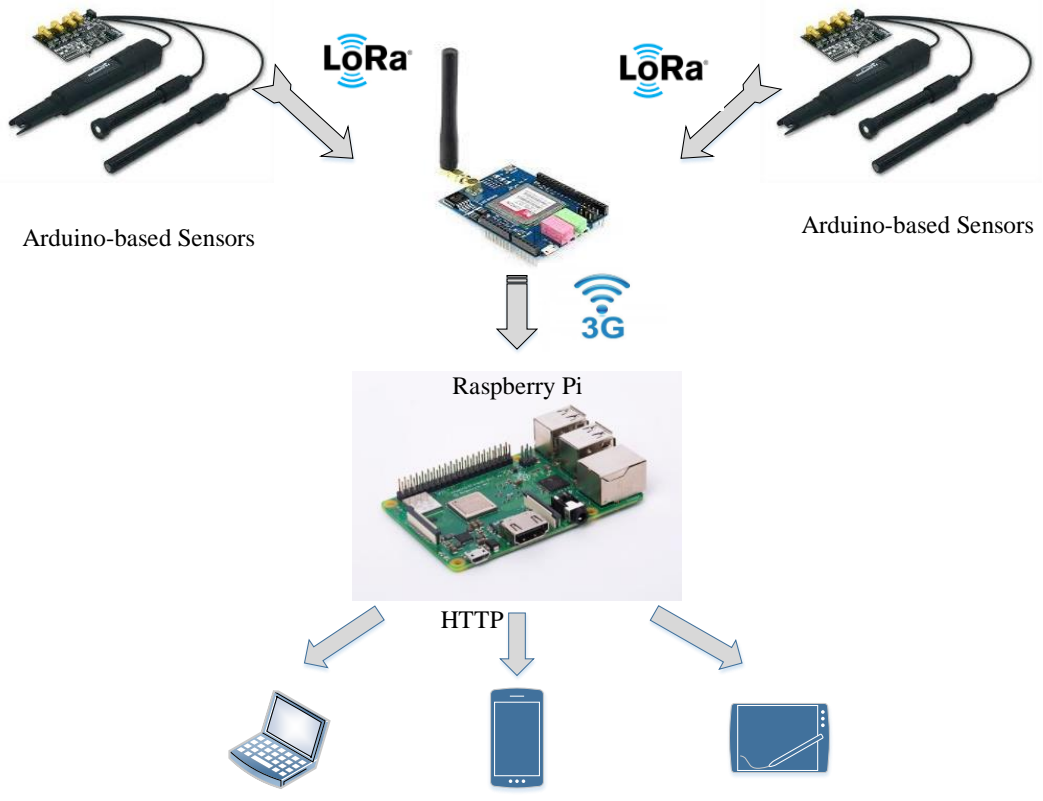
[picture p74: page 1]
Arduino-based Sensors; Raspberry Pi; HTTP

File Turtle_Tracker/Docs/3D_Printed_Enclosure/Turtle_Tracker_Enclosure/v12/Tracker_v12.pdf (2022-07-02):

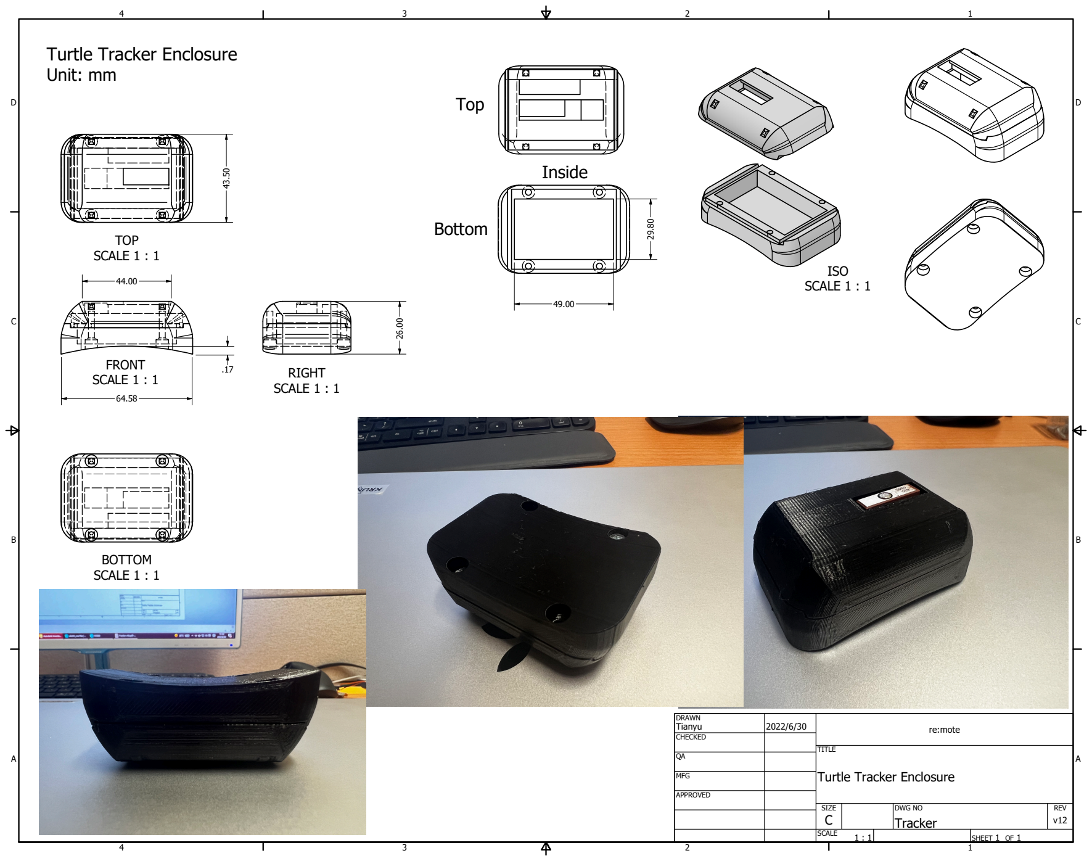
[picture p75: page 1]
SCALE 1 : 1

Turtle Tracker Enclosure
Unit: mm

DRAWN Tianyu | 2022/6/30 | re:mote

CHECKED

MFG

APPROVED

SIZE C | DWG NO Tracker | REV v12

SCALE 1 : 1 | | SHEET 1 OF 1

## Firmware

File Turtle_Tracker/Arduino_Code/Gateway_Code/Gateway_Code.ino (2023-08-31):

/*
  Turtle Tracker Arduino code used in the re-mote setup found at 
  https://gitlab.cas.mcmaster.ca/re-mote
*/

/* ------------------------ Config ------------------------- */

#define GATEWAY_ID 0x64 // Unique Gateway ID, 100(0x64) <= GATEWAY_ID <= 200(0xc8)

// Sever Info
#define HOST "turtletracker.cas.mcmaster.ca"  // Change this to the public IP address / domain of the server's network
#define ENDPOINT "/data"                      // Server HTTP POST endpoint
#define SERVER_PORT 80                        // Server port number

// Length of each line in ToSend.bin: 
// Type,NodeID,TimeStamp,Lat,Lon
// \r\n0d065d1135ca15cd5b07b168de3a
#define BIN_LINE_LENGTH 40

// HTTP Post
#define POST_AMOUNT 4       // Define how many tracker data to read for a single post (Based on testing, 4 is a stable amount for Uno)
#define POST_TIME 2700000     // Time between each post (ms), 2700000ms ~45min
#define GATEWAY_REPORT_TIME 3600000 // Time between each gateway report, 3600000 ~a hour

// SD Card
// Hardware SPI is used by LoRa, so software SPI with different pins is required
#define SD_CS_PIN A5          // SD Card CS Pin
#define SD_SOFT_MISO_PIN A2   // SD Card MISO Pin
#define SD_SOFT_MOSI_PIN A3   // SD Card MOSI Pin
#define SD_SOFT_SCK_PIN A4    // SD Card SCK Pin

// Tinysine 3G Shield
// Two pins conflict with LoRa Shield
// Connect 8 => A1
//         9 => A0
// Config Bandrate to 9600 under "STEP2: 3G Baud Adjustment"
// https://www.tinyosshop.com/index.php?route=information/news&news_id=51
#define SIM3G_EN A1                   // 3G Enable Pin
#define SIM3G_TX 4                    // 3G TX Pin
#define SIM3G_RX 5                    // 3G RX Pin

// 3G Enable Pin Time
// https://www.tinyosshop.com/datasheet/3G%20Shield%20Datasheet.pdf
#define SIM3G_POWER_ON_TIME 180       // 3G Power on time for enable pin (ms)
#define SIM3G_POWER_OFF_TIME 4000     // 3G Power off time for enable pin (ms)

// 3G Timeout
#define SIM3G_HTTP_TIMEOUT 60000       // 3G http timeout (ms)

// Message encoding
// refer to message encoding in this file:
// https://github.com/re-mote-sensing/re-mote/blob/master/Turtle_Tracker/Docs/message_format_turtle_tracker.xlsx
#define REG_LEN 4 // registration message length (in bytes)
#define SEN_LEN 14 // sensor data message length (in bytes)
#define SEN_HEADER_LEN 6 // SEN_BODY_LEN = SEN_LEN - SEN_HEADER_LEN (in bytes)
#define ACK_LEN 3 // ack messgae length (in bytes)
#define DATA_POINT_NUM 19 // the maximum num of data points that can be stored in lora buff
#define DATA_POINT_SIZE 13 // size of one data points (in bytes)
#define REG_TYPE 0x0c // registration type in hex
#define SEN_TYPE 0x0d // sensor data type in hex
#define ACK_SUCCESS 0x00 // first byte in successful ack message

// LoRa
#define LORA_TX_POWER 20      // Output power of the RFM95
#define INVERT_IQ_MODE false  // InvertIQ mode
#define INTERUPT_MODE false   // Use interupt pin when receive a LoRa Message (Arduino Uno does not have enough SRAM)
#define LORA_FREQ 915E6       // Legal frequency in Canada

// Serial
#define PC_BAUDRATE 9600L     // Debug Serial Baudrate
#define SIM3G_BAUDRATE 9600L  // 3G Shield Serial Baudrate

// Debug
#define DEBUG false  // Set to true for debug Serial output, false for no output
#define DEBUG_SERIAL if(DEBUG) Serial // Serial for debuging

/* ------------------------ Librarys ------------------------- */

// LoRa Library
// An Arduino library for sending and receiving data using LoRa radios.
// https://www.arduino.cc/reference/en/libraries/lora/
#include <LoRa.h>

// NeoSWSerial Library
// An efficient replacement for SoftwareSerial, Simultaneous RX & TX
// https://www.arduino.cc/reference/en/libraries/neoswserial/
#include <NeoSWSerial.h>

// SdFat Library
// Provides access to SD memory cards. 
// SPI_DRIVER_SELECT must be 2 in SdFat/SdFatConfig.h
// https://www.arduino.cc/reference/en/libraries/sdfat/
#include "SdFat.h"
#if SPI_DRIVER_SELECT != 2
#error SPI_DRIVER_SELECT must be 2 in SdFat/SdFatConfig.h
#endif  //SPI_DRIVER_SELECT

// MemoryFree Library
// Report memory usage for SRAM debuging
// https://github.com/maniacbug/MemoryFree
#if DEBUG
#include <MemoryFree.h>
#endif

/* ------------------------ Constructors ------------------------- */

NeoSWSerial ss(SIM3G_TX, SIM3G_RX);   // Serial for 3G Shield
// SdFat software SPI
// https://github.com/greiman/SdFat/blob/master/examples/SoftwareSpi/SoftwareSpi.ino
SoftSpiDriver<SD_SOFT_MISO_PIN, SD_SOFT_MOSI_PIN, SD_SOFT_SCK_PIN> softSpi;
// Speed argument is ignored for software SPI.
#define SD_CONFIG SdSpiConfig(SD_CS_PIN, DEDICATED_SPI, SD_SCK_MHZ(0), &softSpi)

// Length of variable in postToServerWithBuffer()
const unsigned int CHTTPSOPSE_LENGTH = 22 + sizeof(SERVER_PORT) + sizeof(HOST); // Command:22 + $SERVER_PORT:3 + $HOST:29
const unsigned int msgBody_LENGTH = 2 + (BIN_LINE_LENGTH-2)*POST_AMOUNT; // Command:2 + ($BIN_LINE_LENGTH-2)*$POST_AMOUNT:6
const unsigned int POST_COMMAND_LENGTH = 33 + sizeof(HOST) + sizeof(ENDPOINT) + msgBody_LENGTH; // Command:33 + $HOST:29 + $ENDPOINT:5 + $msgBody_LENGTH

/* ------------------------ Global Variables ------------------------- */

unsigned long lastPost = millis();  // Track what is the last posted time
unsigned long lastReport = millis();  // Track what is the last gateway report time
bool readyToPost = true;            // Ready to post to server
uint8_t trackerSleepCycles = 28;   // Tracker sleep cycle remote control, 28 for ~30min
uint16_t serialNum = 0; // count how many messages has been sent.

/* ------------------------ Setup ------------------------- */

void setup() {
  DEBUG_SERIAL.begin(PC_BAUDRATE); // Start Debug Serial

  // Reset the 3G shield then turn it off
  pinMode(SIM3G_EN, OUTPUT);
  powerOn3G();
  delay(8000);  // Delay will ensure the 3G is fully turned on
  powerOff3G();
  
  // Start 3G Serial
  ss.begin(SIM3G_BAUDRATE);
  DEBUG_SERIAL.println(F("3G Ok"));

  // Start SD and create ToSend.bin
  createToSendFile(); 

  // Register gateway itself
  registerTracker((uint8_t)GATEWAY_ID);

  // Start LoRa
  if (!LoRa.begin(LORA_FREQ)) {
    DEBUG_SERIAL.println(F("LoRa init failed. Check your connections."));
    while (true);
  }
  LoRa.setTxPower(LORA_TX_POWER); // maximum tx power to get longest range
  //LoRa.setSpreadingFactor(12); // maximum SF to get longest range
  LoRa.enableCrc(); // Enables the LoRa module's built in error checking
  DEBUG_SERIAL.println(F("LoRa init succeeded."));
  
  #if INTERUPT_MODE == true
  // Enable the following three line to enable onReceive with interupt pins DIO0(D2)
  LoRa.onReceive(onReceive);
  LoRa.onTxDone(onTxDone);
  LoRa_rxMode();
  #endif
  
  DEBUG_SERIAL.println(F("Gateway initialized successfully!"));
}

/* ------------------------ Loop ------------------------- */

void loop() {
  // Post to server every POST_TIME ms
  if (readyToPost && (millis() - lastPost) > POST_TIME) {
    if (postToServerWithBuffer()){ // Post data under ToSend.bin
      resetToSend(); // Reset ToSend.bin
    }else{
      DEBUG_SERIAL.println(F("No data to post"));
    }
    lastPost = millis(); // Reset lastPost to current time
    readyToPost = false;
  }

  // Report gateway itself with serial number to check if gateway is working
  // (GPS time and coords has not been impenment yet)
  if ((millis() - lastReport) > GATEWAY_REPORT_TIME){ // Every GATEWAY_REPORT_TIME ms
    reportGateway();
    lastReport = millis(); // Reset lastReport to current time
    readyToPost = true;
  }

  #if INTERUPT_MODE == false
  int packetSize = LoRa.parsePacket();
  String result;
  if (packetSize) {
    onReceive(packetSize);
  }
  #endif
}

/* ------------------------ Callback Functions ------------------------- */

// If LoRa received any message, it will interrupt any current execution line,
// then begin call this onReceive function
void onReceive(int packetSize) {
  // filter by size
  if (packetSize != REG_LEN && (packetSize - SEN_HEADER_LEN) % DATA_POINT_SIZE != 0) {
    return;
  }
  
  DEBUG_SERIAL.print(F("Size: "));
  DEBUG_SERIAL.println(packetSize);
  
  // read type and sensor#
  uint8_t typeAndSensor = (uint8_t) LoRa.read();
  uint8_t type = typeAndSensor >> 4;

  #if DEBUG
  DEBUG_SERIAL.print("Type: ");
  printByte(type);
  DEBUG_SERIAL.println();
  #endif
  
  // do action according to message type
  switch (type) {
    // <--- CASE: Registration ---> //
    case REG_TYPE: {
      // read nodeID
      uint8_t nodeID = (uint8_t) LoRa.read();
      // read serial number (16 bits = 2 bytes)
      uint8_t serialNum[2];
      serialNum[0] = (uint8_t) LoRa.read();
      serialNum[1] = (uint8_t) LoRa.read();
      // read data debug
      #if DEBUG
      DEBUG_SERIAL.print(F("nodeID: "));
      printByte(nodeID);
      DEBUG_SERIAL.println();
      DEBUG_SERIAL.print(F("serialNum: "));
      printByte(serialNum[0]);
      printByte(serialNum[1]);
      DEBUG_SERIAL.println();
      #endif
      // covert data to string
      DEBUG_SERIAL.print(F("nodeID: "));
      DEBUG_SERIAL.println(String(nodeID));
      DEBUG_SERIAL.print(F("serialNum: "));
      DEBUG_SERIAL.println(String(* (uint16_t*) serialNum)); 
      // register
      registerTracker(nodeID);
      // send ACK
      sendAck(nodeID);     
      break;
    }
      
    // <--- CASE: Sensor Data ---> //
    case SEN_TYPE: {
      // read nodeID
      uint8_t nodeID = (uint8_t) LoRa.read();
      // read serial number (16 bits = 2 bytes)
      uint8_t serialNum[2];
      serialNum[0] = (uint8_t) LoRa.read();
      serialNum[1] = (uint8_t) LoRa.read();
      // read battery percentage
      uint8_t batteryPercentage = (uint8_t) LoRa.read();
      // read datapoint count
      uint8_t datapointCount = (uint8_t) LoRa.read();
      
      for (uint8_t i = 0; i < datapointCount; i++) {
        // read unixTime
        uint8_t unixTime[4];
        unixTime[0] = (uint8_t) LoRa.read();
        unixTime[1] = (uint8_t) LoRa.read();
        unixTime[2] = (uint8_t) LoRa.read();
        unixTime[3] = (uint8_t) LoRa.read();
        // read latitude
        uint8_t latitude[4];
        latitude[0] = (uint8_t) LoRa.read();
        latitude[1] = (uint8_t) LoRa.read();
        latitude[2] = (uint8_t) LoRa.read();
        latitude[3] = (uint8_t) LoRa.read();
        // read longitude
        uint8_t longitude[4];
        longitude[0] = (uint8_t) LoRa.read();
        longitude[1] = (uint8_t) LoRa.read();
        longitude[2] = (uint8_t) LoRa.read();
        longitude[3] = (uint8_t) LoRa.read();
        // read tempurature
        uint8_t tempurature = (uint8_t) LoRa.read();

        // add data into buffer
        addDataByte(
                type,
                nodeID, 
                serialNum,
                batteryPercentage,
                datapointCount,
                unixTime,
                latitude,
                longitude,
                tempurature
                );
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

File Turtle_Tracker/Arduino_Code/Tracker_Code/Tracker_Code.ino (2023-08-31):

/*
  Turtle Tracker Arduino code used in the re-mote setup found at 
  https://gitlab.cas.mcmaster.ca/re-mote
*/

/* ------------------------ Config ------------------------- */

#define NODE_ID 0x01 // Unique Node ID

// Pinout
#define GPS_TX 3 // GPS TX Pin
#define GPS_RX 4 // GPS RX Pin
#define GPS_EN 6 // GPS Enable Pin
#define LoRa_RESET 9 // LoRa reset Pin

// Timeout
#define GPS_TIMEOUT 80000 // GPS read timeout (ms) (Average read time 31sec on GP735T)
#define ACK_TIMEOUT 10000 // ack waiting time (ms) for sending sensor data
#define DEFAULT_SLEEP_CYCLES 14 // Number of loops the tracker will sleep 8*SLEEP_CYCLES_MUTIPLIERs, for 112 is ~15min
#define MAX_SLEEP_CYCLES 168 // Maximum sleep time, ~3 hours
#define SLEEP_CYCLES_MUTIPLIER 8 // SLEEP_CYCLES in lowpower mode will always mutiply this number

// Message encoding
// refer to message encoding in this file:
// https://github.com/re-mote-sensing/re-mote/blob/master/Turtle_Tracker/Docs/message_format_turtle_tracker.xlsx
#define REG_LEN 4 // registration message length (in bytes)
#define SEN_LEN 14 // sensor data message length (in bytes)
#define ACK_LEN 3 // ack messgae length (in bytes)
#define DATA_POINT_NUM 19 // the maximum num of data points that can be stored in lora buff
#define DATA_POINT_SIZE 13 // size of one data points (in bytes)
#define BUF_SIZE DATA_POINT_NUM*DATA_POINT_SIZE // no more than 256 bytes (maximum len of a lora message)
#define REG_AND_NUM 0xc0 // registration message type and sensor number 0
#define SEN_AND_NUM 0xd0 // sensor data message type and sensor number 0

// LoRa
#define LORA_TX_POWER 20 // Output power of the RFM95
#define INVERT_IQ_MODE false // currently use InvertIQ mode, set it to false to stop INVERTIQ
#define LORA_RegTemp 0x3c
#define LORA_RegIrqFlag2 0x3f
#define LORA_FREQ 915E6// legal frequency in Canada

// Serial
#define PC_BAUDRATE 9600L   // Debug Serial Baudrate
#define GPS_BAUDRATE 9600L  // Debug GPS Baudrate

// Debug
#define DEBUG false // Set to true for debug output, false for no output
#define DEBUG_SERIAL if(DEBUG) Serial // Serial for debuging

/* ------------------------ Librarys ------------------------- */

// LoRa Library
// An Arduino library for sending and receiving data using LoRa radios.
// https://www.arduino.cc/reference/en/libraries/lora/
#include <LoRa.h>

// NMEA and ublox GPS parser for Arduino, configurable to use as few as 10 bytes of RAM
// https://github.com/SlashDevin/NeoGPS/blob/master/src/NMEAGPS.h
#include <NMEAGPS.h>

// Overwrite the GPS hardware's configuration
#include <TurtleTracker_UBX_2022.h>

// NeoSWSerial Library
// An efficient replacement for SoftwareSerial, Simultaneous RX & TX
// https://www.arduino.cc/reference/en/libraries/neoswserial/
#include <NeoSWSerial.h>

// Lightweight low power library for Arduino.
// https://github.com/rocketscream/Low-Power
#include "LowPower.h"

/* ------------------------ Constructors ------------------------- */
// Official usage provided by <NMEAGPS.h>
NeoSWSerial gpsPort(GPS_TX, GPS_RX); 
NMEAGPS gps;
gps_fix fix;

/* ------------------------ Global Variables ------------------------- */

boolean ackReceived = false; // flag used in automatically detecting ack
long lastTime = 0; // Save the timestamp for the last GPS fix data
uint16_t serialNum = 0; // count how many messages (registration or sensor data) has been sent.
uint8_t trackerSleepCycles = DEFAULT_SLEEP_CYCLES; // initially, set the tracker sleep cycles to default.

// a circular buf for storing the body (data points) of the lora message
// maximum supported size is 256, as lora can only packet 256 bytes into one message.
typedef struct CircularBuffer {
  uint8_t bufArray[BUF_SIZE] = {};
  uint8_t writeIndex = 0;
  uint8_t readIndex = 0;
  uint8_t bufLen = 0;
} circularBuffer;
circularBuffer loraBuf;

/* ------------------------ Setup ------------------------- */
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

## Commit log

2018-08-16 Updated README for arduino-motes
2018-08-17 Added link to arduino-motes README about wiki
2019-05-01 Add lora mesh arduino project.
2019-05-21 Added "working" (almost, kinda) arduino code for DO sensor and 3G shield that communicate via LoRa
2019-05-31 Added Arduino code for GPS gateway
2019-06-04 Update RyanTyrrell19/Notes/GPS/Planner.md, UBLOX on Arduino.md files
2019-06-04 Deleted UBLOX on Arduino.md
2019-06-04 Update RyanTyrrell19/Code/UBLOX on Arduino
2019-06-06 Upload New File
    [LoRa_MESH_Test.xlsx]
2019-06-07 Added working sensor end node and 3G gateway node code
2019-06-13 Added finished sensor end node and gateway node arduino code. It still needs to be cleaned up quite a bit
2019-06-18 Added a bunch of comments and a to do list to the Arduino gateway code
2019-06-19 Added a bunch of comments to the sensor end node code
2019-06-19 Small change to sensor end node code
2019-06-19 Combined functions for reading from Atlas Scientific sensors
2019-06-21 Added another error code to sensor data message acknowledgement
2019-06-24 Deleted RyanTyrrell19/Notes/LoRa/Testing/LoRa Antenna RSSI Test (2)/RSSI_Data.xlsx
    [RSSI_Data.xlsx]
2019-06-24 Deleted RyanTyrrell19/Notes/LoRa/LoRa_MESH_Test.xlsx, RyanTyrrell19/Notes/LoRa/LoRa_test_data.txt, RyanTyrrell19/Notes/LoRa/MESH_Module_Test.md, RyanTyrrell19/Notes/LoRa/MESH_Module_Test_2.0.md, Ryan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
    [LoRa_MESH_Test.xlsx, RSSI_Test_Data.xlsx]
2019-07-03 Changed Arduinos to use new location sending method
2019-07-29 Added support for an enable pin on Atlas Scientific EC sensor
2019-07-29 Added temperature and salinity compensation to Atlas Scientific sensors
2019-07-30 Added ability to select cs pin for sd card on gateway
2019-08-09 Update RyanTyrrell19/Notes/Turtle Tracker/Turtle_Tracker_Specs.md, RyanTyrrell19/Notes/Turtle Tracker/Turtle_Trackers_Breakdown.md, RyanTyrrell19/Notes/Turtle Tracker/Enclosure/Waterproofing_and_Moun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
2019-08-09 Added support for Atlas Scientific pH sensor
2019-08-09 Added Files to RyanTyrrell19/
    [Battery.ipt, BatteryV2.0002.ipt, BatteryV2.ipt, BatteryV2.stl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]
2019-08-09 Deleted RyanTyrrell19/Code/Turtle Trackers/Turtle Trackers/.vs/Turtle Trackers/v16/.suo, RyanTyrrell19/Code/Turtle Trackers/Turtle Trackers/.vs/Turtle Trackers/v16/Solution.VC.db, RyanTyrrell19/Code/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
2019-08-16 This folder contains measurements of current of all the sensors, nodes, and pin-connections during the sleep and awake mode. Also, battery life calculation is performed based on these readings.
2019-08-16 Current Drawn Readings
2019-08-16 Gateway Node Current Draw
2019-08-19 Moved some files around, changed Arduino code to only have one .ino file
2019-08-21 Housing unit for Fona3G, Arduino UNO, SD Card Adapter, and DHT sensor
2019-08-21 3D Model Design
    [LID_Enclosure_Box.ipt]
2019-08-21 Housing unit for Arduino Nano, GPS, Turbidity, DO, EC/pH, Temperature, LoRA Mesh
2019-08-21 Lid of the box
    [END_NODE_-_LID_SIMPLE.ipt]
2019-08-21 How to print 3D model
2019-08-21 Contains .stl files for all the 3D printed parts
2019-08-21 Solar Module from Adafruit and Battery Enclosure Box
2019-08-21 Contains instruction on how to assemble all the hardware to fit in the enclosing box
2019-08-21 Instructions to set-up battery operated nodes
2019-08-21 This file contains all the information regarding the product, assembly, and 3D model
2019-08-21 Assembly-Pin Connections, Enclosure Box, Power Consumption
2019-08-21 Read to assemble all the modules
2019-08-21 Instructions on how to assemble solar power module
2019-08-21 End Nodes, Gateway Node and Solar Power Module
2019-08-21 3D model - can house a 6600mAh Li-ion battery as well
2019-08-21 Lists the amperage of all the modules and battery life of a 4400mAh battery
2019-08-21 End Node Current Measurement
2019-08-21 Gateway Current Drawn by each module and also the pin connections
2019-08-21 Deleted unncessary files
    [END_NODE_-_LID_SIMPLE.ipt, END_NODE_-_LID_SIMPLE.stl, END_NODE_SIMPLE.ipt, END_NODE_SIMPLE.stl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]
2019-08-22 Reorganized arduino-motes repository
    [Battery.ipt, BatteryV2.0002.ipt, BatteryV2.ipt, BatteryV2.stl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]
2019-08-22 More reorganizing
    [END_NODE_-_LID_SIMPLE.ipt, END_NODE_-_LID_SIMPLE.stl, END_NODE_SIMPLE.ipt, END_NODE_SIMPLE.stl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]
2019-08-22 Combined water quality and turtle tracker base arduino code
2019-08-22 Set-up of all the sensors with Arduino Board
2019-08-22 Pin connections explained
2019-08-22 Setup and Battery Optimization
2019-08-22 Update Gateway Assembly.md
2022-03-30 Add part list for water sensor
2022-03-30 update part list for water sensor
2022-07-02 Update Turtle Tracker Codes & Docs
    Update Gateway Code
    - Binary Format Post to Server
    - Add more Comments
    Add Work in Progress Docs and Libraries
    [Enclosure-Base.ipt, Enclosure-Top.ipt, Tracker.dwg, Tracker.iam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]
2022-07-06 add message format
    [message_format_turtle_tracker.xlsx]
2022-07-08 fix code based on jul 8 code review
    [message_format_turtle_tracker.xlsx]
2022-08-09 Update Water Sensor Code
    Gateway:
    - 3G off when not using
    - HTTPS to HTTP
    End Node:
    - Turn off sensors
    - Config mode
2022-12-25 Update Water Sensor Code
    Update libraries
    Add apiKey support
    Add RTC, TPL5110 support
2023-06-04 Update Documentations
    - Add details to water sensor docs
    - Corp images
    - Update specification
2023-08-31 Updating and reorganizing files
    Merge Server, Motes, Jupyter analysis repos into one repo
    [Battery.ipt, BatteryV2.0002.ipt, BatteryV2.ipt, BatteryV2.stl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]
2024-11-07 Update 3D Printing Info
    [re:mote-test4.stl]
